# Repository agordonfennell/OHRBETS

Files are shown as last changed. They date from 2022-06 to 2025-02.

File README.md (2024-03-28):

# OHRBETS (Open-source Head-fixed Rodent Behavior Experimental Training System)
<p align="center">
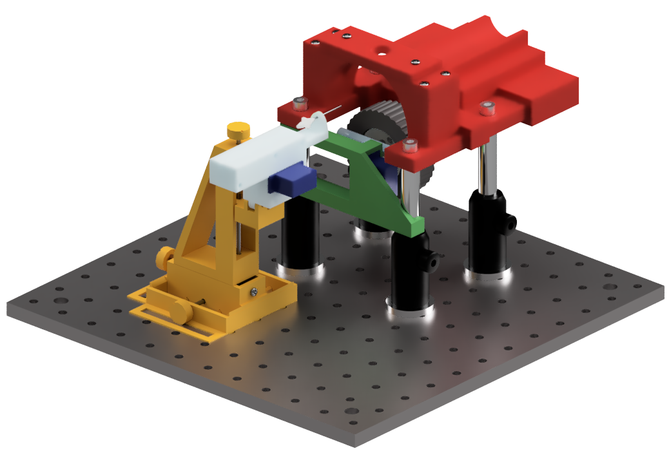
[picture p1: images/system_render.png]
  
</p>

Accompany to [Gordon-Fennell et. al. 2023 eLife](https://elifesciences.org/articles/86183)

## Overview
Here we make available an ecosystem of open-source hardware and software for operant and consumption experiments in head-fixed mice. For operant responding, mice rotate a wheel in one of two directions and operant responding is gated using a mechanical wheel break. For consumption, mice consume liquid solutions from a metal lick spout and access to the spout is gated using retraction and extension of the spout. The system also includes optional multi-spout hardware that allows fixed access to 1 of 5 spouts. The system presented here offers a scalable option for these behavioral approaches and is compatible with head-fixed imaging techniques including 2-photon imaging.  

The hardware consists of 3d printed and other low-cost components including micro servos that can be easily assembled with our detailed step-by-step guide. The system utilizes an Arduino Mega to control hardware including servos, solenoids, and tone generators, and to record behavioral events including licks and wheel rotation. Session parameters and behavioral events are recorded using a PC connected to the Arduino via USB. 

The Arduino software includes programs written in the Arduino language. We have included multiple scripts for different behavioral approaches including operant conditioning and multi-spout brief access. We have also included scrips used to setup for behavior and trouble shoot the system.  

The Analysis software includes programs written in R and relies on user created spreadsheets. We have included a universal decoder that parses the data produced by the Arduino. We have also included scripts for analyzing data produced by the generic operant conditioning and multi-spout brief access task Arduino programs.

We will continue to update this repository and add additional hardware and software. We welcome contributions that add on to our system for different behavioral designs.  
## DOI: 
- 10.5281/zenodo.8320175

## Associated Pre-Print
- [bioRxiv](https://www.biorxiv.org/content/10.1101/2023.01.13.523828v1)

## Up to Date Resources
- [Purchase List](https://docs.google.com/spreadsheets/d/1kFgsOy1gAFHM2E8M-DSgPSi6Y7Lr8sis6cbQqSb2ZY4)
- [3d Printing File Key](https://docs.google.com/spreadsheets/d/1pzRUh2JkpAaJyb1kA9NBVjSYz8nG3GPTu3c0QVQwKCg)

## Tinkercad Models (#OHRBETS)
- [Full Respository](https://www.tinkercad.com/users/elZH8v8MJf0-adam-gordon-fennell)
- [OHRBETS_assembly](https://www.tinkercad.com/things/58vTdDu0pfz)
- [OHRBETS_components_filament](https://www.tinkercad.com/things/1Yv3k1L5hwq)
- [OHRBETS_components_resin](https://www.tinkercad.com/things/6Ztq3dLU4Uj)
- [OHRBETS_components_multispout](https://www.tinkercad.com/things/cckeigB3ydE)
- [OHRBETS_arduino_enclosure](https://www.tinkercad.com/things/ki4dcN9vabO)
- [OHRBETS_mount_syringe](https://www.tinkercad.com/things/ft7A0Lh4chg)
- [OHRBETS_mount_solenoid](https://www.tinkercad.com/things/eRxwZDRHmDL)

## Contributors
Adam Gordon-Fennell (University of Washington), Garret Stuber (University of Washington)

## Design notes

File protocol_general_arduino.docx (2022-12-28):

# General Arduino Protocol

This document contains a general overview of using Arduino and a brief review of the types of scripts that we include with the system.

A detailed overview of the Arduino language and program structure are beyond the scope of this protocol. For a more detailed overview refer to the Arduino website (link (https://www.arduino.cc/reference/en/)).

## General Overview

- Arduinos operates independently of the computer connected to it. Once a script is uploaded to the Arduino, the script will run continuously until the Arduino is loses power or is reset.
- Arduinos can be reset through the following methods
  - Opening a serial connection with the Arduino (e.g. opening the serial monitor in the Arduino IDE or opening a serial connection through python).
  - Connecting and disconnecting the USB
  - Reset button on the Arduino

Note: Make sure you are aware of the current state of the Arduino program. When using behavioral programs, reset the Arduino prior to head-fixing a subject to ensure that the program is in the starting state.

- Each script we have included with this system is composed of 3 major sections
  - Definitions:
    - Each variable is defined. Crucially, the datatype must be set as the variable is defined and will limit the range of values the variable can represent.
    - Dependencies are included
    - Values for many parameters are set
  - void setup ():
    - code that is ran once from top to bottom
    - Behavioral scripts include a line that waits for a serial command from the computer to begin.
  - void loop ():
    - code that is ran repeatedly from top to bottom

## IDE Overview

Serial Monitor

### Main screen

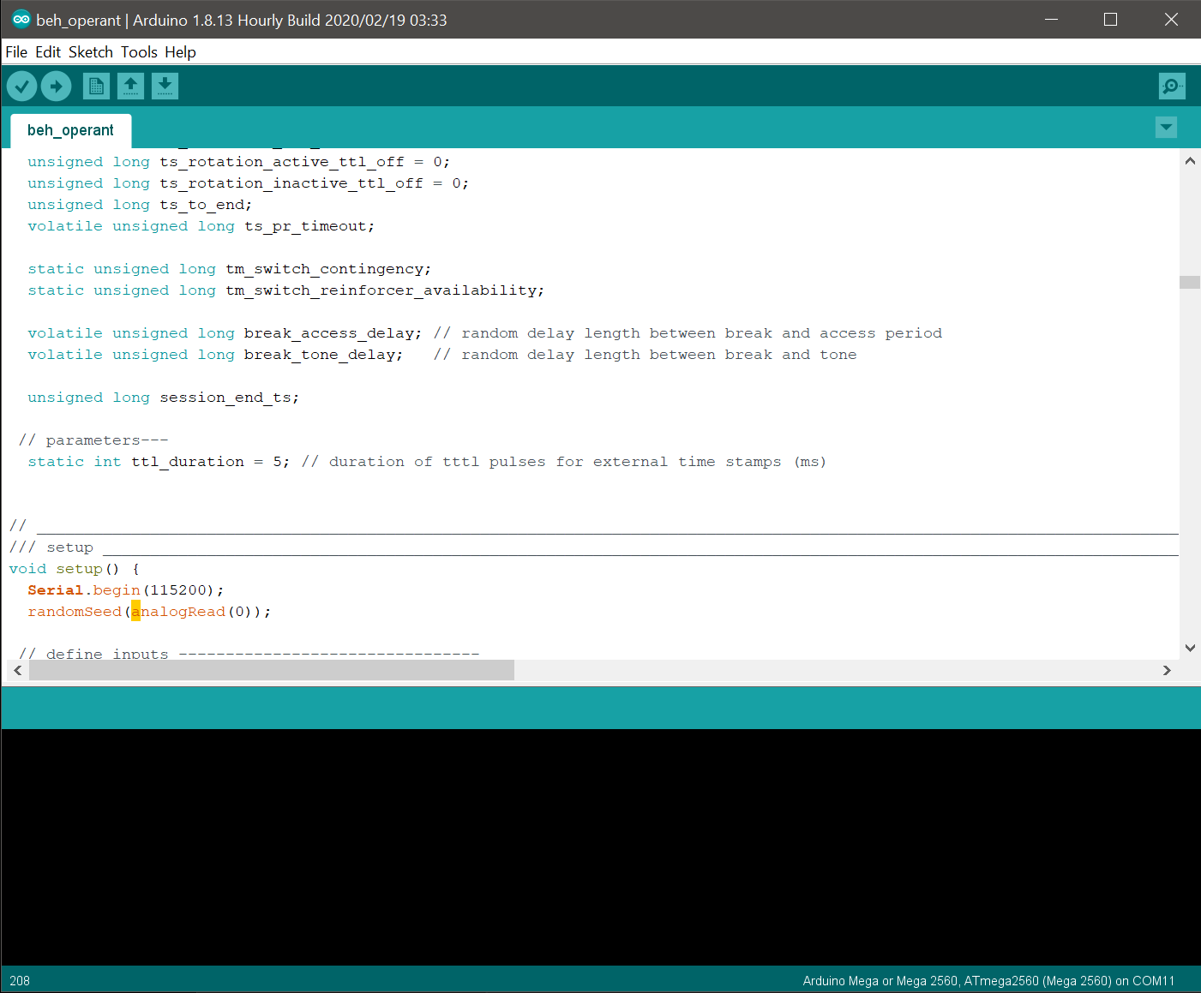
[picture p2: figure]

Upload (Verify script and send to current Arduino)

Verify (check for Arduino syntax)

COM for current Arduino

Arduino Script

Serial Monitor

### Tools menu

Manage libraries to download external libraries

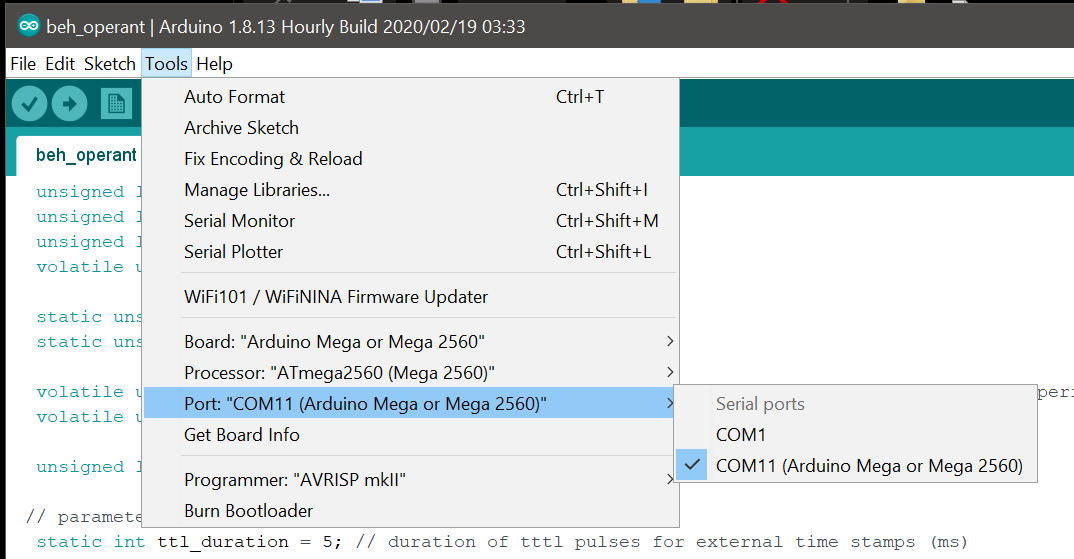
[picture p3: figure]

Set board type of current Arduino

Set current Arduino based on COM port

## Scripts and Serial Monitor Overview

- Arduino scripts (suffix = .ino) must be contained within folders of the same name as the file.
- To open an Arduino script, double click on the .ino file.
- To send script to Arduino, click the “Upload” button
  - You cannot send an script to an Arduino with an active serial connection from another instance of the IDE or external program. Make sure to close these out before attempting to send script to the Arduino.
- To interact and/or monitor the Arduino, click the Serial Monitor button
  - This will connect to the Arduino and reset the script currently on the Arduino (edits to the script will not be reflected on the Arduino until the script is uploaded).
- Serial Monitor

Button to send string to Arduino

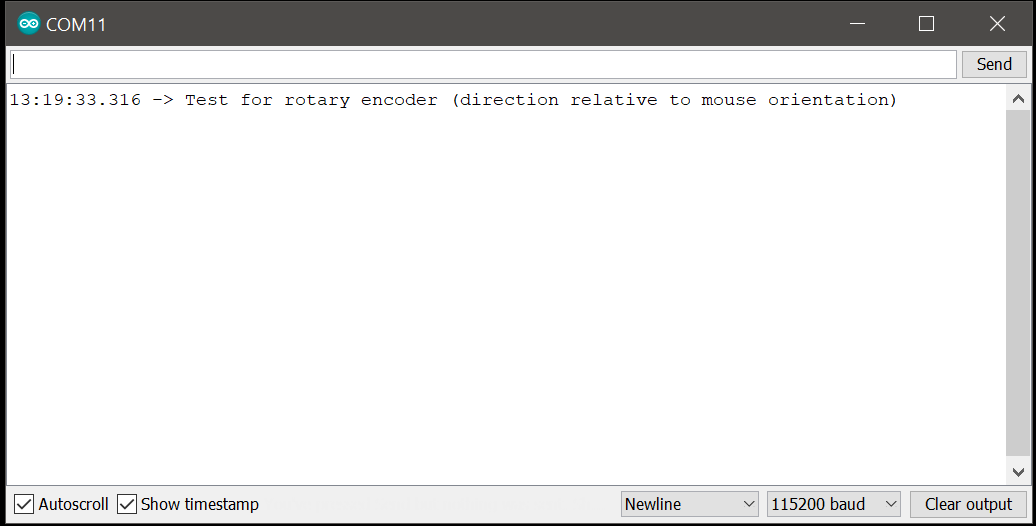
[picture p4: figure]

Baud rate for serial communication

String to send

to Arduino

Display for serial prints from Arduino

  - Multiple “helper” scripts use the Serial Monitor string input to control the state of the Arduino. To do this, simply type out a string in the box to the left of the “Send” button and click Send to communicate it to the Arduino.
- Check to ensure that the baud rate is set correctly.
  - Baud rate is set within the Arduino program with Serial.begin(baudrate)
  - For programs included with this system, the default baud rate is set to 115200. Other scripts may use different buad rates.
  - If the baud rate is not set correctly, the strings produced by the Arduino will not be decoded properly and will be printed with jumbled symbols

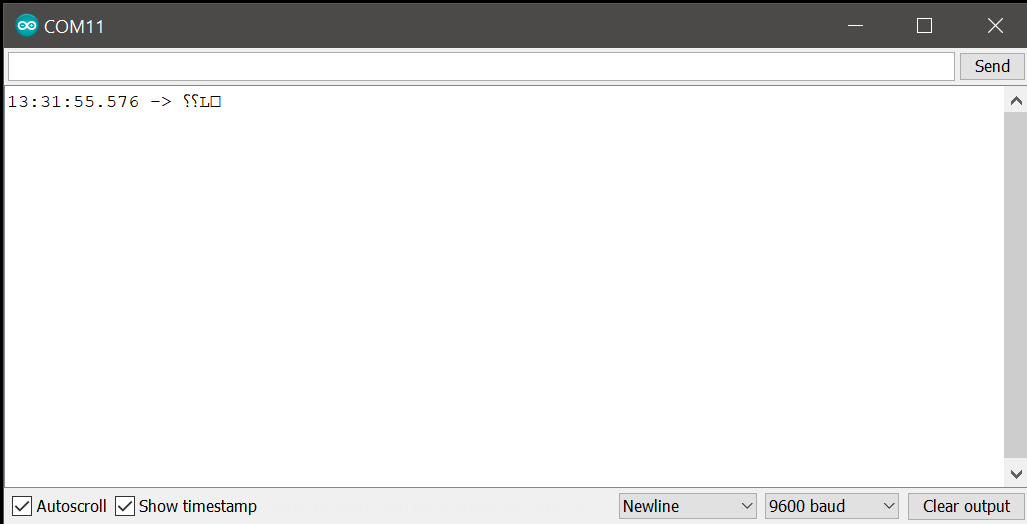
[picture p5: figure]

- Behavioral scripts will require that a string is sent to the Arduino before the program begins
  - For testing a program, open the Serial Monitor and click the “Send” button to send an empty string and start the behavioral program.
  - During real behavioral sessions, we will use a python script to open the serial connection, start the Arduino, and record the serial (see Python section below).

## External libraries

- You will need to install the MPR121 library in order to compile and upload scripts that contain lick detection.
  - Installed through Tools > Manage Libraries > search MPR121

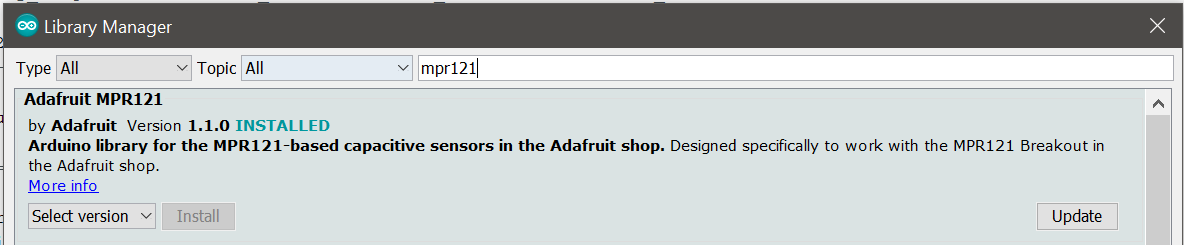
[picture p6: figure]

  - Make sure to install with all dependencies

## write_serial.py Overview

- The write_serial.py script is used to restart the Arduino, send a start command, and then record the Serial prints while the Arduino is running.
- Can be run using any IDE or directly from the command line. We used Sublime Text 3 for the example shown here.
- There are 3 parameters that you will need to set:

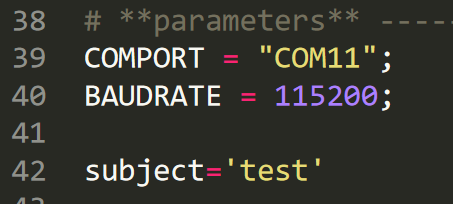
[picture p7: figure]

  - COMPORT: string identifier for the comport of the Arduino (check the Arduino Tools > Port for Com ID)
  - BAUDRATE: integer baud rate (must match comport set in Arduino script)
  - Subject: string for subject ID (must be unique for each session)
- When executed the program will do the following
  - Generate file name based on current date and subject id:
    - General format: yyyy_mm_dd_subject
    - If there is a conflict, a string suffix will be added for the time with the following format: _hhmmss
  - Open serial communication with Arduino based on COMPORT and BAUDRATE
  - Generate and then append a csv file with each line printed by the Arduino each
    - Note: the program only works with numeric and space prints from the Arduino and will not work with strings of characters
  - Closes serial communication and stops executing when a “0” is printed in the first position of the print from the Arduino.
    - Note: If you edit the Arduino scripts, do not include a print with 0 in the first position

## Raw data structure

All behavioral programs are written to have a uniform data structure consisting of two columns of numerical data that fall into 3 categories

1. Parameters: stable parameters for the session (1 row). These values print once at the start of the session.
  a. First column: parameter ID
  b. Second column: parameter value
2. Dynamic parameters: parameters can change values at different points throughout a session (2 rows / change in parameter)
  a. First column first and second rows: parameter ID
  b. Second column first row: time stamp for the onset of the current parameter (ms)
  c. Second column second row: current value of the parameter
3. Events: events occurring during the behavioral session
  a. First column event ID
  b. Second column timestamp (ms)
- All of the IDs for events, parameters, and dynamic parameters are listed in key_events.csv. This table is used to decode data within each raw Arduino csv file.
  - If you add additional events, follow the format outlined here in the Arduino print, and add a corresponding row to the key_events.csv file.

## Trouble shooting quick guide:

- Cannot upload script to Arduino

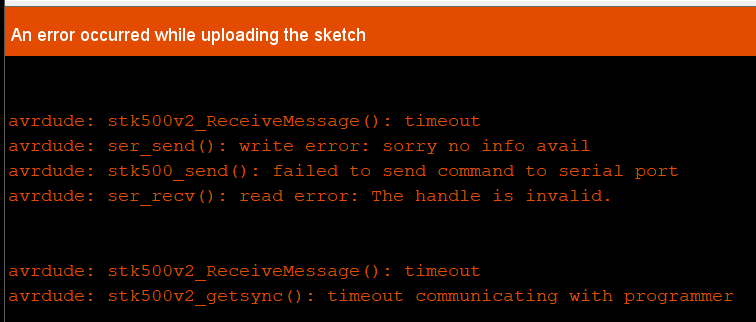
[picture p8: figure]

  - Check to ensure that all other serial communication with the Arduino is closed. If the problem persists, disconnect / reconnect Arduino USB
- Strange symbols in serial print via Serial Monitor
  - check baud rate in script and serial connection
- Cannot connect to Arduino with write_serial.py

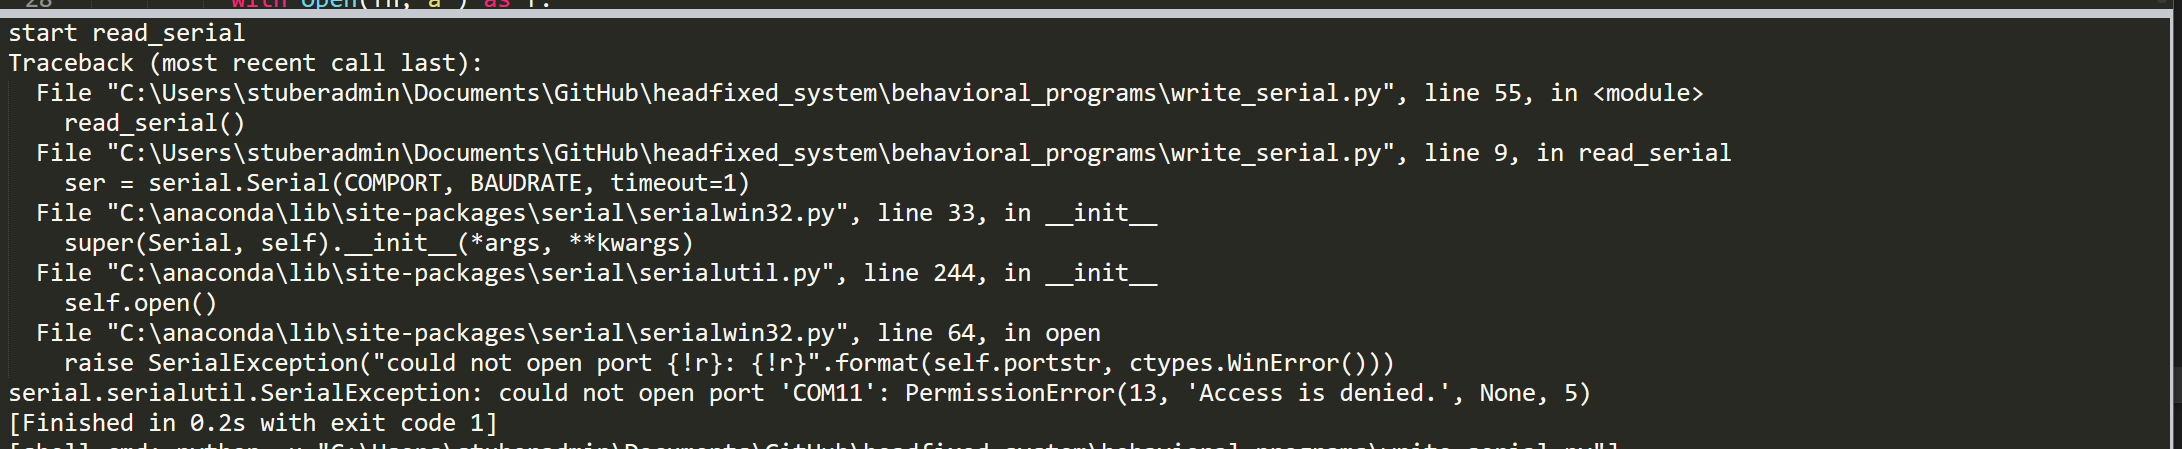
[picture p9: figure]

  - Check to ensure that all other serial communication with the Arduino is closed. If the problem persists, disconnect / reconnect Arduino USB
  - Check to ensure that COMPORT is set to the correct Arduino
- UnicodeDecodedError with write_serial.py

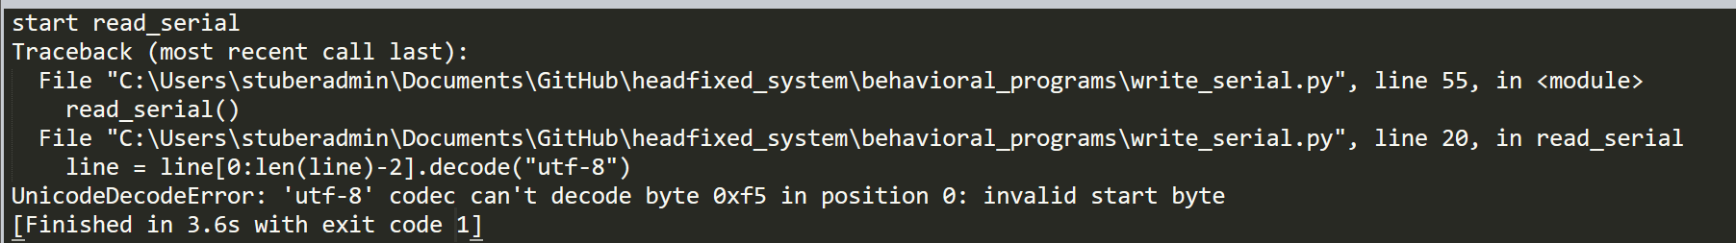
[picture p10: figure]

  - Check to ensure that baud rate in write_serial.py matches baud rate set in Arduino script
  - Check to ensure that COMPORT is set to the correct Arduino

Write_serial.py Arduino script

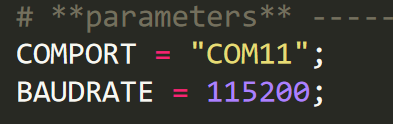
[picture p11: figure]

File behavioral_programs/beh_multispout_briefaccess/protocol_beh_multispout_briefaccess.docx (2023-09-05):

Protocol for beh_multispout_briefaccess.ino

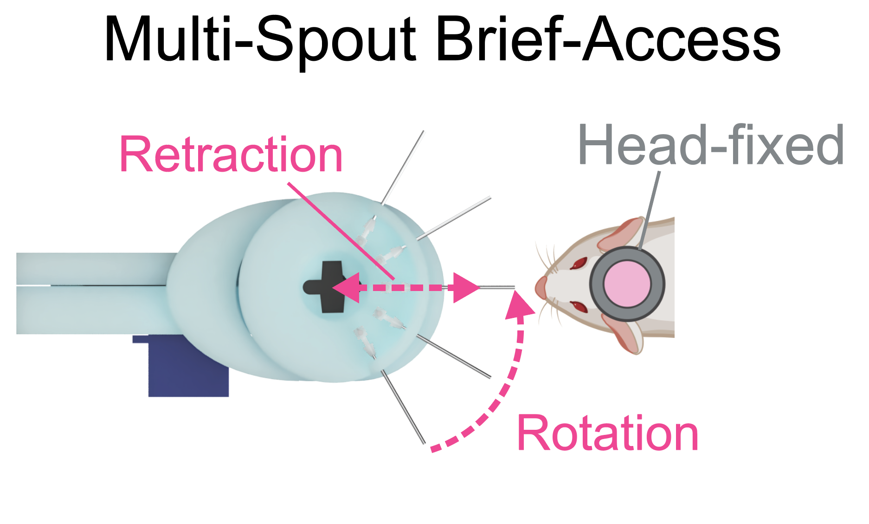
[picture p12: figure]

Program purpose: allows subject fixed windows of access time to one of multiple spouts.

Access windows can include free-access consumption or fixed volume delivery.

Preparation Instructions:

1) Around once per week, calibrate the solenoid open duration for each solenoid by following protocol_helper_calibratesolenoid. Save the solenoid open duration(s) somewhere convenient in a vector format with 1 value per solenoid (e.g. 3 elements for 3 spouts: each vector would look like {value, value, value}).
2) Fill the solution line(s) by following protocol_helper_opensol.
3) Optional: connect BNC or TTL outputs from the arduino console to the external hardware.

Initial Calibration of Rotation and Extension

After assembling the hardware, it is useful to perform an initial calibration to determine estimates for the rotation and extension of each spout. These values will serve as a starting point but may be changed slightly at the start of each day.

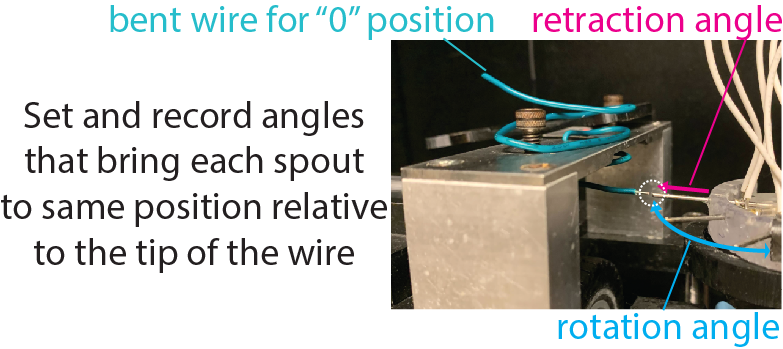
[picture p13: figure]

1. Use a length of wire and wrap it over a head stage such that the end of the wire sits roughly where the nose of a mouse would be located.
2. Upload manual_servo.ino and open the Serial Monitor.
3. First, fully extend the retractable spout.
  1. Enter the pin for the servo used for retraction and send over serial (default = 9).
  2. Enter 180 for a fully extended starting position.
4. Next, move the servo to determine the rotation angle for each spout.
  1. Enter the pin for the servo used for the radial multi-spout head and send over serial (default = 11).
  2. Rotate the head to the first spout (right most spout from the mouse’s perspective) so it is at a right angle relative to the head-stage. Start with sending a value of 0 over the serial, then progressively increase until the spout is at a right angle. Record this value.
  3. Use the micro-positioner to move the spout so it is in line with the piece of wire and almost touching.
d. For the remaining spouts, send new serial values to change the rotation of the head to align each spout with the tip of the wire and record the angle for each spout (you should have one angle for each spout). With default hardware, the spouts should be roughly 30 degrees apart.
5. To calibrate the extension for each spout
  1. Open the beh_multispout_briefaccess.ino program.
  2. Enter the servo_radial_degs values obtained from step 4 (format: {#,#,#};, with one # for each spout).
  3. Enter default values for servo_retract_extended_degs ({180,180,180}; with one value for each spout).

Arduino Setup Instructions:

1) Open the program
2) Set the parameters and input / output pins
- Carefully read the comments next to each variable
3) Upload script to arduino by clicking the “Upload” arrow button on the top left corner
- The arduino will now have the script running on it and it will wait until a start command is sent over serial.

Arduino Test Instructions:

Test the program at the start of each day to ensure all hardware is working and events are being recorded correctly.

1) To test the program, open serial monitor by clicking the “Serial Monitor” button on the top right corner

Note: If you do not see this text printed in the serial monitor, see troubleshooting arduino software document.

2) Start the arduino program by clicking the button to send an empty string over serial.

### Note on lick detection with high-molar NaCl

Special care needs to be taken to ensure that the capacitive touch sensor is accurately detecting licks when using high-molar NaCl solutions. Some systems have produced poor detection on specific spouts during mouse licking. After confirming that all hardware works with finger touches, watch subject licking carefully while monitoring lick detection. If there is a problem with lick detection on a particular spout, do not use this spout for high molar NaCl or build a new multi-spout head. Future improvements to the design will be posted in the accompanying GitHub.

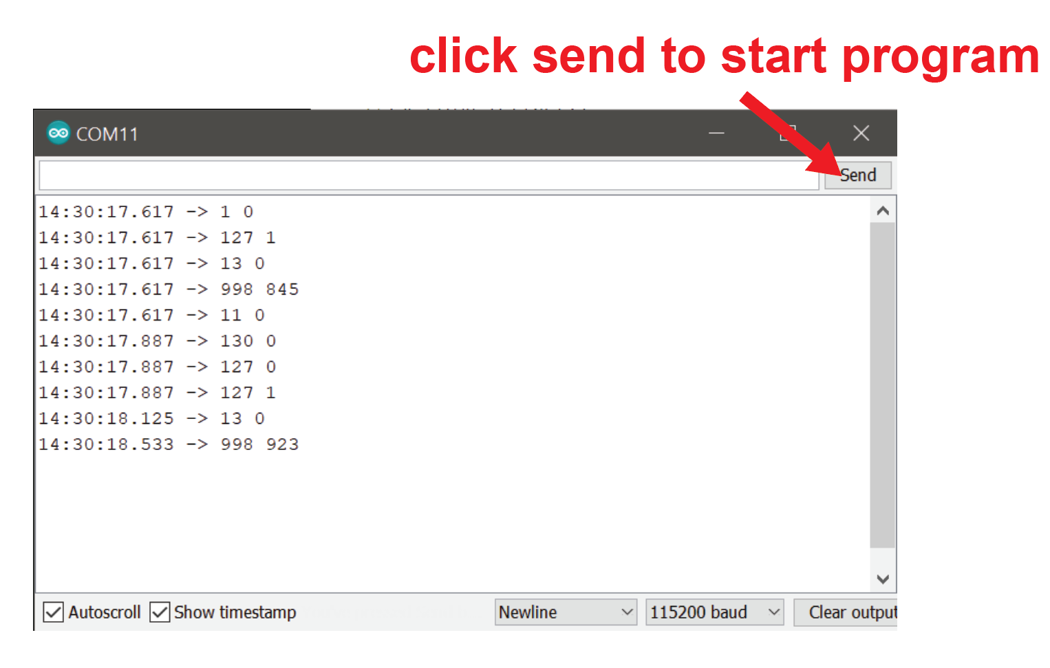
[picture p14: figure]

3) Watching the Serial Monitor while interacting with the hardware, check to ensure that…
  a) Rotating the wheel in the intended active direction produces code 81.
  b) Rotating the wheel in the intended inactive direction produces code 71.
  c) Touching the spout produces code 30 + current spout (e.g. 31 for spout 1, 32 for spout 2, etc.).
  d) Rotation of the wheel in the active direction that reaches the fixed ratio triggers the intended sequence of events (break, tone, spout extension, liquid delivery or external TTL signal).
  e) If performing progressive ratio, check to ensure that the cost of the reinforcer increases as intended.
  f) Rotation in the inactive direction that reaches the fixed ratio triggers the intended sequence.
4) For multi-spout systems, if the intended spout is not detecting touch, check other spouts to see if they are detecting touch. If you find that a spout other than the one rotated towards the mouse is detecting touch, then check the servo_retract_radial_degs vector to ensure the values are correct for your head, and check to ensure the servo is working properly.
  a) If liquid is emerging from the wrong spout, then check the pinSol vector to ensure that the correct pins are included for your system.
5) Reset the arduino by closing and reopening the Serial Monitor, and then close Serial Monitor prior to the session.

Arduino Run Instructions:

1) Open the write_serial.py program (shown here using Sublime Text 3)

- Set the COMPORT and BAUDRATE to match the arduino script

Arduino comport is shown in the tools drop down menu

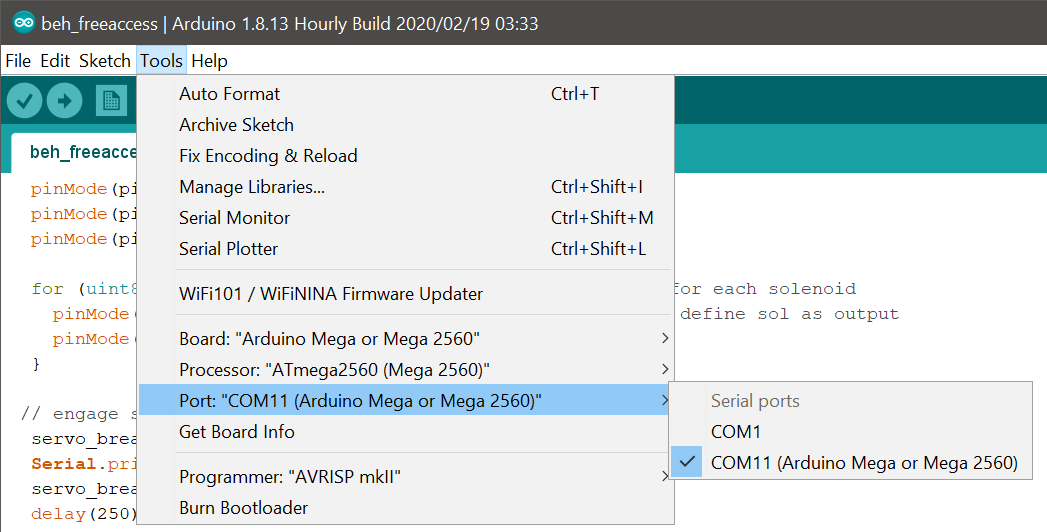
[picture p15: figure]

Arduino baudrate is set with “Serial.begin” call

- Set the subject name for the session in the python program

Note: See general arduino software document for more details about the functionality of the write_serial.py program.

2) After the program and hardware have been tested, head-fix the animal.
3) Set the spout position as shown in this diagram:

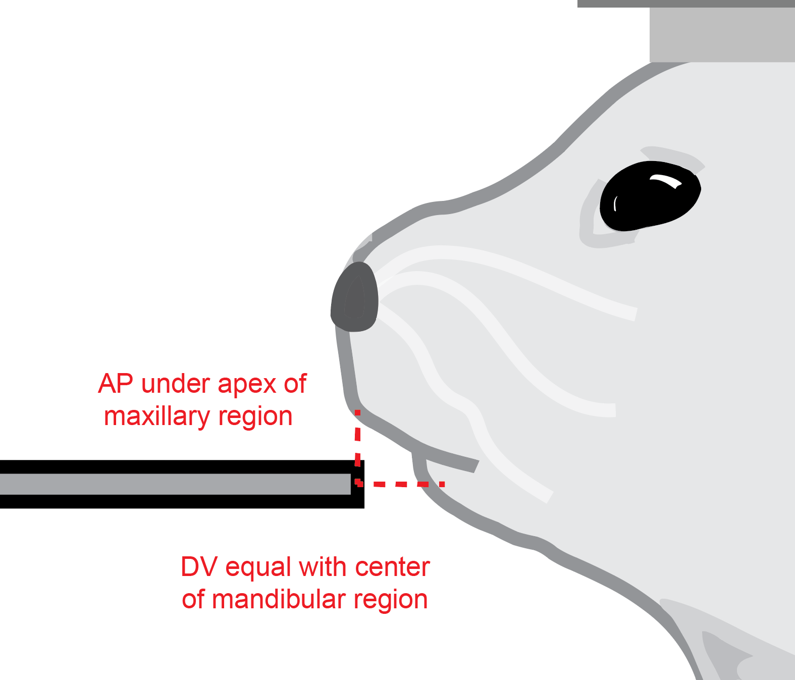
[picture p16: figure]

Note: See link (https://www.facebase.org/mouseanatomy/) for examples of mouse face anatomy

4) Run the python program (Cntrl + B for Sublime Text 3).
- Values should begin to print with the start of the session, and will continue to print during recorded events.

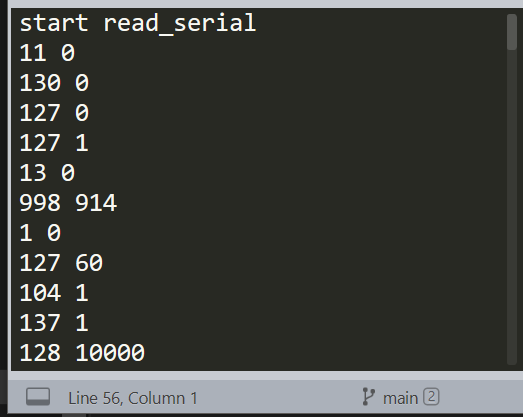
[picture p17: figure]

Note: If you see an error, refer to the general arduino software document for troubleshooting tips.

5) At the end of the session, the spout will retract (if using a retractable spout), the brake will engage, and the python script will print “stop read_serial”).
6) Remove subject from head-fixation.
7) Restart arduino prior to subsequent subjects by opening / closing the arduino Serial Monitor. Otherwise, the spout will extend for the next subject and could result in poking the subject.

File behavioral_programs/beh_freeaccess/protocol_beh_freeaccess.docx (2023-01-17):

Protocol for beh_freeaccess.ino

Program purpose: free-access consumption for a set session duration.

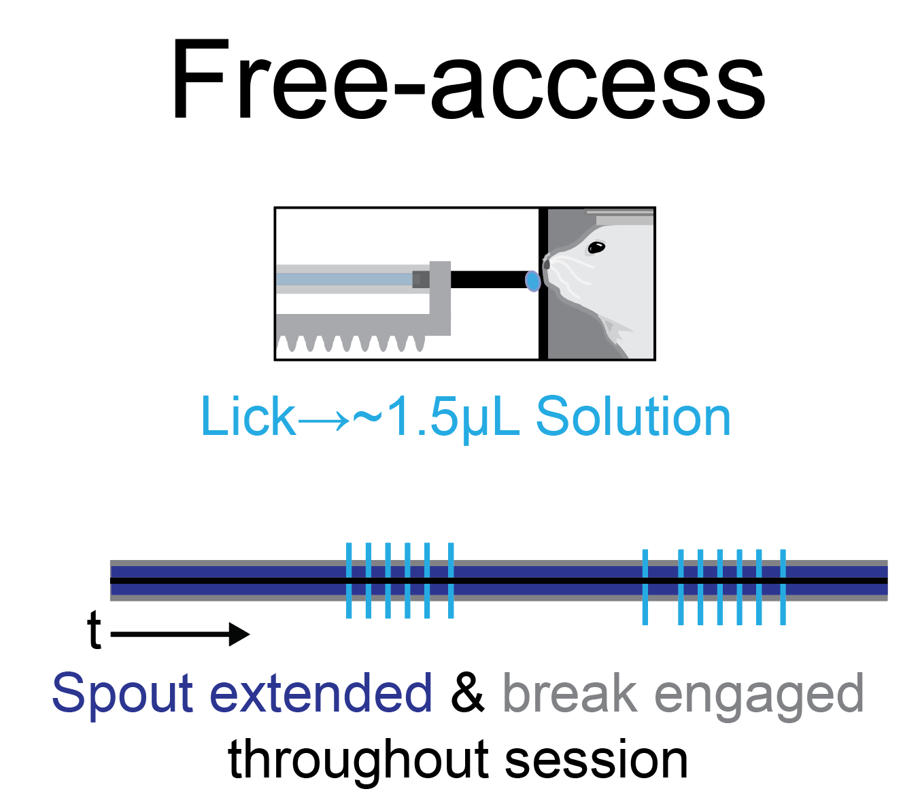
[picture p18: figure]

Preparation Instructions:

1) Around once per week, calibrate the solenoid open duration by following protocol_helper_calibratesolenoid. Save the solenoid open duration(s) somewhere convenient in a vector format with 1 value per solenoid (e.g. 3 vectors for 3 spouts: each vector would look like {value, value, value}).
2) Fill the solution line(s) by following protocol_helper_opensol.
3) Optional: connect BNC or TTL outputs from the arduino console to the external hardware.

Arduino Setup Instructions:

1) Open the program
2) Set the parameters and pins

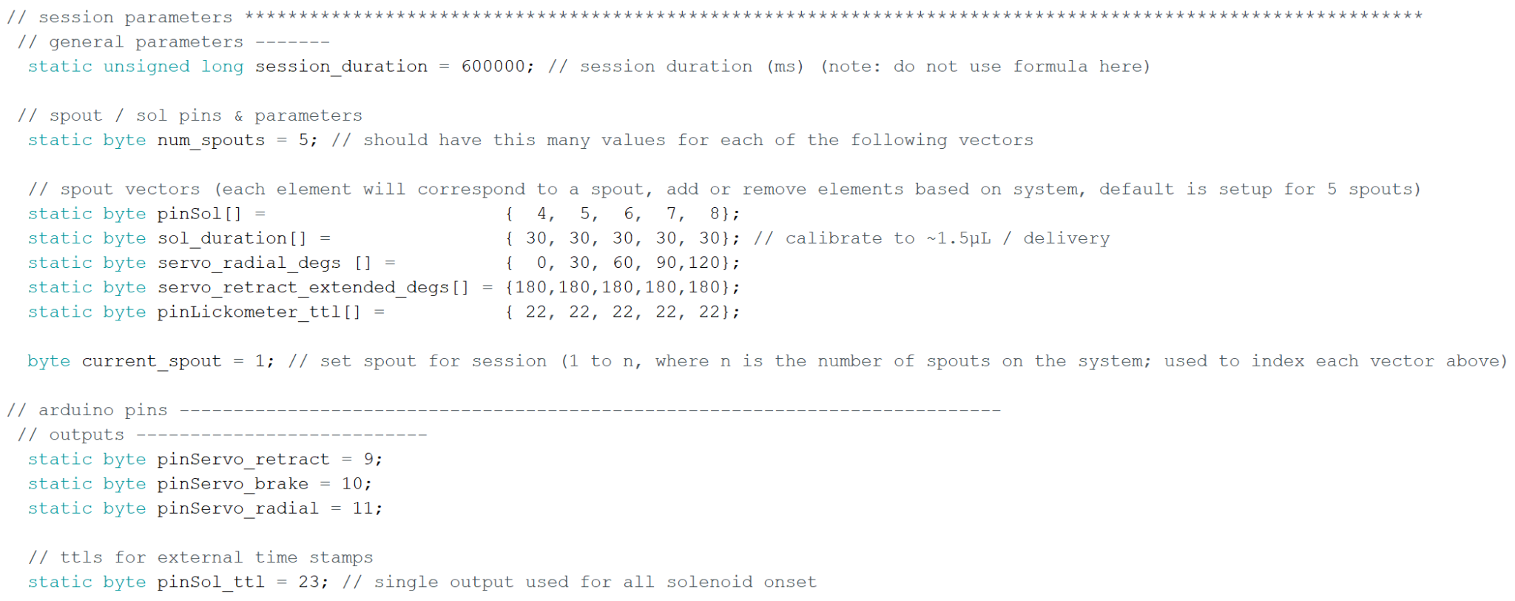
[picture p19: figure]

- For spout / sol pins & parameters, you will need 1 value for each of the spout / sol that your system has. This way you can set current_spout to perform free-access licking on any spout (e.g. current_spout 1 uses the first value for each vector, current_spout 2 uses the second value, etc.).
  - Note: If your system only has 1 spout, then change the vectors to be a length of 1 (e.g. pinSol[] = {4}; sol_duration[] ={30}; etc. ).
- It is fine if you do not have a radial servo, as long as nothing is plugged into the corresponding pin
- pinLickometer_ttl is used as an external timestamp for the onset of licks on each spout
- pinSol_ttl is used as an external timestamp for onset of any solenoid opening
3) Upload script to arduino by clicking the “Upload” arrow button on the top left corner.
- The arduino will now have the script running on it and it will wait until a start command is sent over serial.

Arduino Test Instructions:

Test the program at the start of each day to ensure all hardware is working and events are being recorded correctly.

1) To test the program, open the serial monitor by clicking the “Serial Monitor” button on the top right corner.

Note: If you do not see this text printed in the serial monitor, see troubleshooting arduino software document.

2) Start the arduino program by clicking the button to send an empty string over serial.

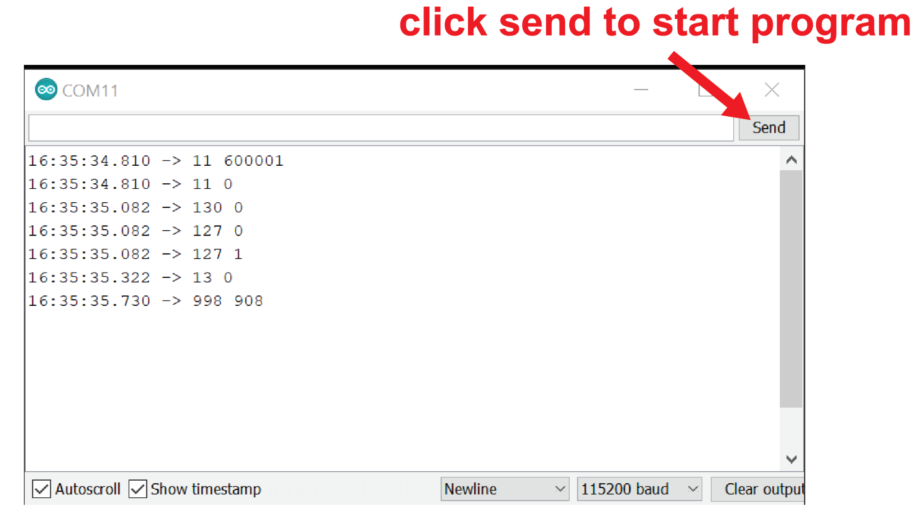
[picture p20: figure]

3) Manually touch the spout gently with the tip of an ungloved finger several times to ensure that licks are being detected, solenoids are opening, and liquid is being delivered from the lick spout. Each touch on the current_spout should lead to events printed in the Serial Monitor, opening of the corresponding solenoid (confirmed with concurrent sound, or vibrations when solenoid is touched during opening), and a droplet of liquid emerging from the spout.
  a) The serial code should be 30 + current_spout (e.g. if current_spout = 2, then the code should be 32).
  b) For multi-spout systems, if the intended spout is not detecting touch, check other spouts to see if they are detecting touch. If you find that a spout other than the one rotated towards the mouse is detecting touch, then check the servo_retract_radial_degs vector to ensure the values are correct for your head, and check to ensure the servo is working properly
  c) If liquid is emerging from the wrong spout, then check the pinSol vector to ensure that the correct pins are included for your system.
4) Reset the arduino by closing and reopening the Serial Monitor. Close Serial Monitor prior to the session.

Arduino Run Instructions:

1) Open the write_serial.py program (shown here using Sublime Text 3)

- Set the COMPORT and BAUDRATE to match the arduino script

Arduino comport is shown in the tools drop down menu


Arduino baudrate is set with “Serial.begin” call

- Set the subject name for the session within the python program

Note: see general arduino software document for more details about the functionality of the write_serial.py program

2) After the program and hardware have been tested, head-fix the animal.
3) Set the spout position as shown in this diagram:


Note: See link (https://www.facebase.org/mouseanatomy/) for examples of mouse face anatomy

4) Run the python program (Cntrl + B for Sublime Text 3).
- Values should begin to print with the start of the session, and will continue to print during recorded events


Note: If you see an error, refer to the general arduino software document for troubleshooting tips

5) At the end of the session, the spout will retract (if using a retractable spout) and the python script will print “stop read_serial”
6) Remove subject from head fixation
7) Restart arduino prior to subsequent subjects by opening / closing the arduino Serial Monitor. Otherwise, the spout will extend for the next subject and could result in poking the subject

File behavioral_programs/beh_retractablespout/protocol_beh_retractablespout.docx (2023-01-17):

Protocol for beh_retractablespout.ino

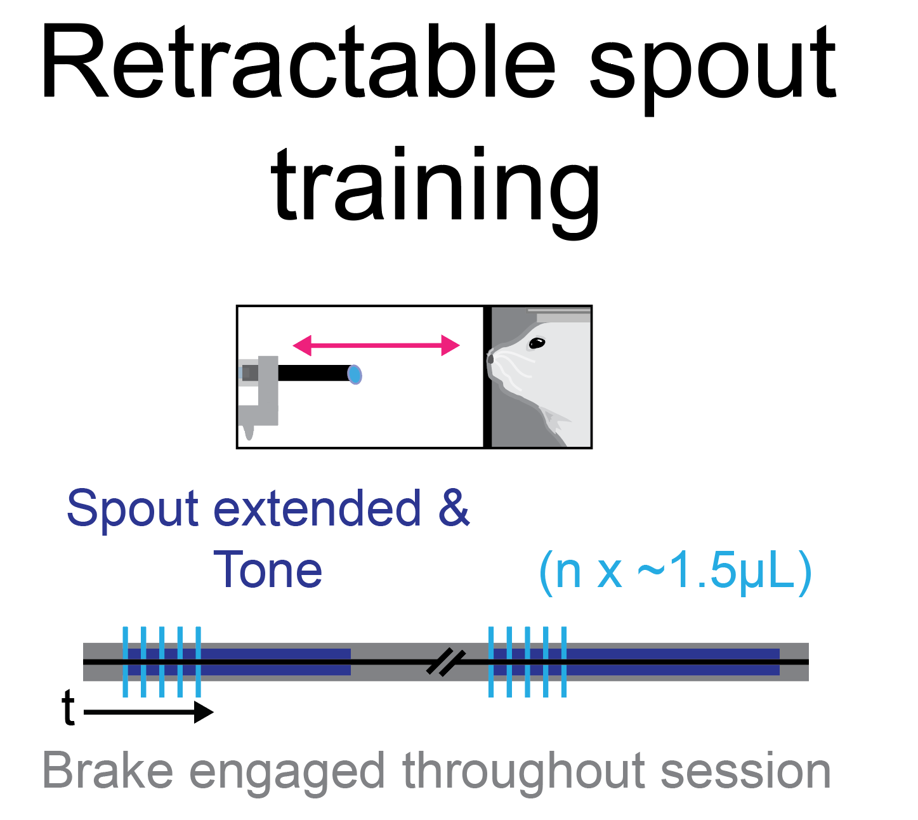
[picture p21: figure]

Program purpose: delivery of a fixed volume of solution with options for retractable spout training and Pavlovian Conditioning.

Preparation Instructions:

1) Around once per week, calibrate the solenoid open duration by following protocol_helper_calibratesolenoid. Save the solenoid open duration(s) somewhere convenient in a vector format with 1 value per solenoid (e.g. 3 values for 3 spouts: each vector would look like {value, value, value}).
2) Fill the solution line(s) by following protocol_helper_opensol.
3) Optional: connect BNC or TTL outputs from arduino console to external hardware

Arduino Setup Instructions:

1) Open the program
2) Set the parameters and pins (see Arduino script for all parameters / comments)

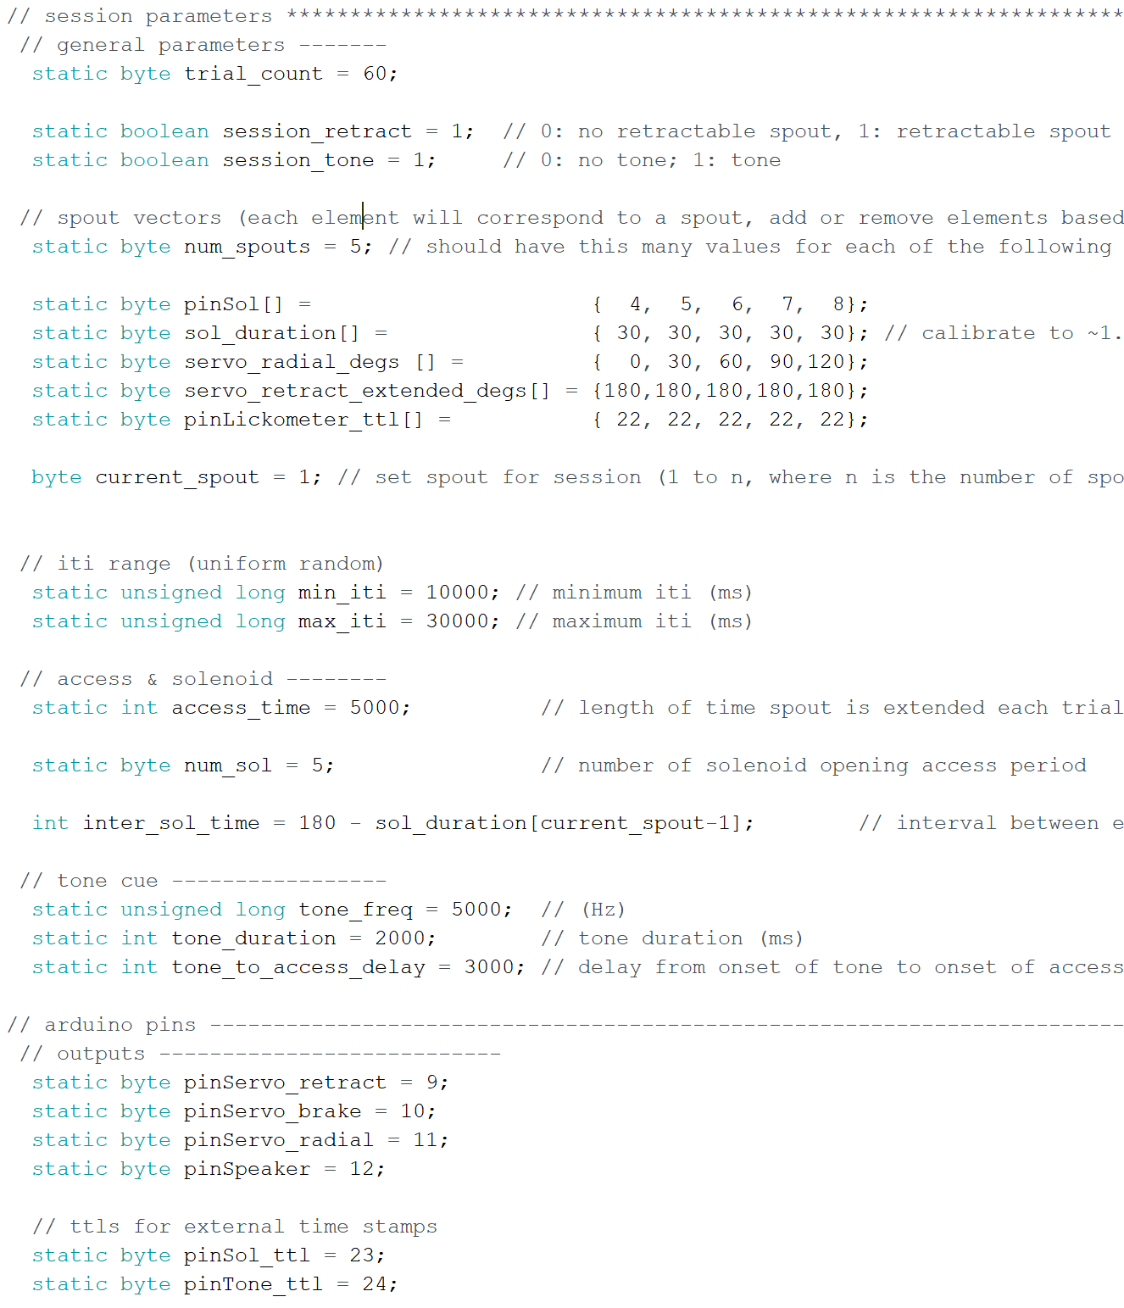
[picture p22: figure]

- Use the tone_duration and tone_to_access_delay to set up the timing for tones and access period / liquid delivery.
- For spout / sol pins & parameters, you will need 1 value for each of the spout / sol that your system has. This way you can set current_spout to perform free-access licking on any spout (e.g. current_spout 1 uses the first value for each vector, current_spout 2 uses the second value, etc.).
  - Note: If your system only has 1 spout, then change the vectors to be a length of 1 (e.g. pinSol[] = {4}; sol_duration[] ={30}; etc.).
- It is fine if you do not have a radial servo, so long as nothing is plugged into the corresponding pin.
- pinLickometer_ttl is used as an external timestamp for onset of licks on each spout.
- pinSol_ttl is used as an external timestamp for onset of any solenoid opening.
- pinTone_ttl is used as an external timestamp for the tone (high for the duration of the tone).
3) Upload script to arduino by clicking the “Upload” arrow button on the top left corner
- The arduino will now have the script running on it and it will wait until a start command is sent over serial.

Arduino Test Instructions:

Test the program at the start of each day to ensure all hardware is working and events are being recorded correctly.

1) To test the program, open serial monitor by clicking the “Serial Monitor” button on the top right corner

You should then be presented with this screen:

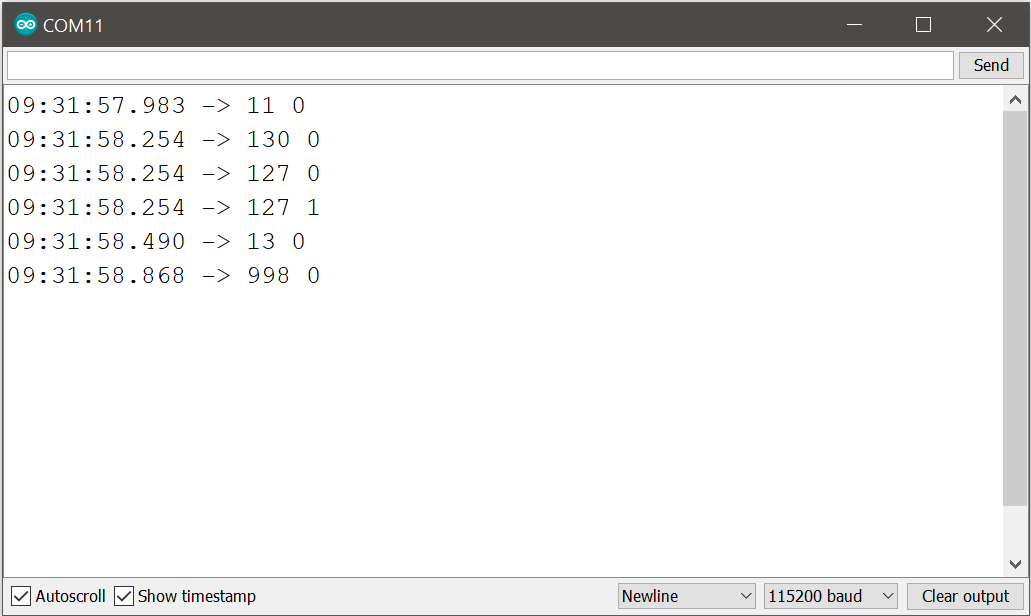
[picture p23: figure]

Note: If you do not see this text printed in the serial monitor, see troubleshooting arduino software document.

2) Start the arduino program by click the button to send an empty string over serial


3) Wait for the trial to begin (tone indicated with code 51, spout extension with code 13, solenoid opening with 18) and check to ensure that liquid is coming out of the tip of the spout. Next, manually touch the spout gently with the tip of an ungloved finger several times to ensure that licks are being detected (indicated with code 30 + current_spout).
  a) For multi-spout systems, if the intended spout is not detecting touch, check other spouts to see if they are detecting touch. If you find that a spout other than the one rotated towards the mouse is detecting touch, then check the servo_retract_radial_degs vector to ensure the values are correct for your Multi-Spout Head, and check to ensure the servo is working properly.
  b) If liquid is emerging from the wrong spout, then check the pinSol vector to ensure that the correct pins are included for your system.
4) Reset the arduino by closing and reopening the Serial Monitor, and then close Serial Monitor prior to the session.

Arduino Run Instructions:

1) Open the write_serial.py program (shown here using Sublime Text 3)

- Set the COMPORT and BAUDRATE to match the arduino script

Arduino comport is shown in the tools drop down menu


Arduino baudrate is set with “Serial.begin” call

- Set the subject name for the session within the write_serial.py

Note: See general arduino software document for more details about the functionality of the write_serial.py program

2) After the program and hardware have been tested, head fix the animal.
3) Set the spout position as shown in this diagram:


Note: See link (https://www.facebase.org/mouseanatomy/) for examples of mouse face anatomy

4) Run the python program (Cntrl + B for Sublime Text 3).
- Values should begin to print with the start of the session, and will continue to print during recorded events.


Note: If you see an error, refer to the general arduino software document for troubleshooting tips.

5) At the end of the session, the spout will retract (if using a retractable spout) and the python script will print “stop read_serial”).
6) Remove subject from head-fixation.
7) Restart arduino prior to subsequent subjects by opening / closing the arduino Serial Monitor. Otherwise, the spout will extend for the next subject and could result in poking the subject.

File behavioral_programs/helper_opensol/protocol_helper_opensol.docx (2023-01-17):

Protocol for helper_opensol.io

Program purpose: helper_opensol.io allows users to rotate the Multi-Spout Head and open individual solenoids for set up or cleanup using one of two modes.

- mode 0:
  - touch spout to open corresponding solenoid, touch again to close
  - set multi-spout angle by sending a degree between 1 and 180 over serial
- mode 2:
  - set multi-spout angle using servo_radial_deg
  - open and close solenoids by sending a serial string with an ID between 1 and n, where n is the number of spouts set in pinSol and stateSol

Note: default program is set up for 5 solenoids / spouts, but can be used for 1 solenoid / spout. See “increasing number of solenoids” section below for instructions for expanding the number of solenoids / spouts.

Use Instructions:

1) Open the program (make sure the program is located in a folder of the same name)
2) Set the parameters and pins

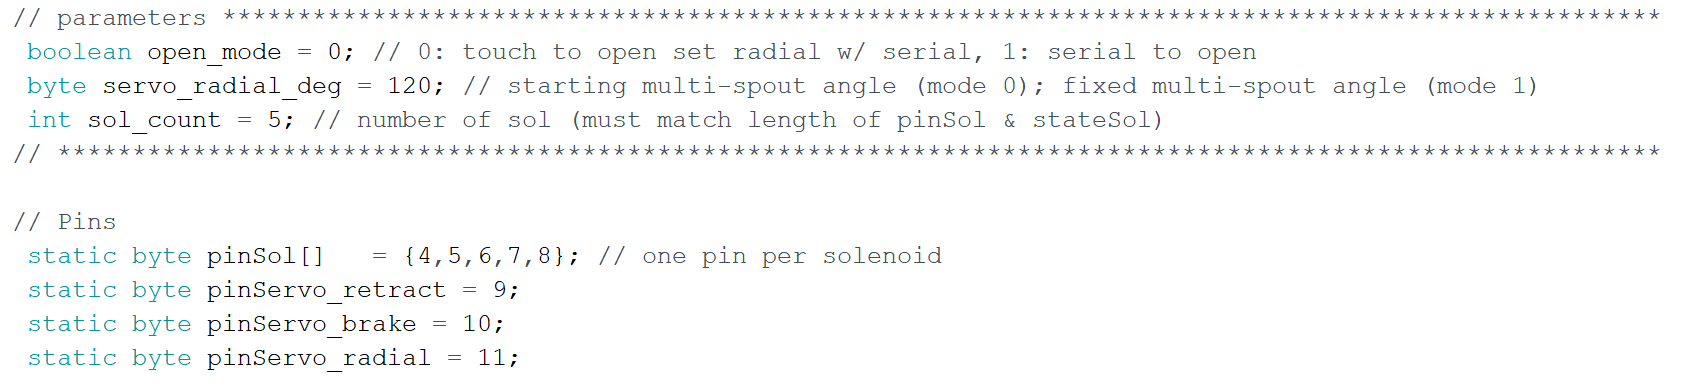
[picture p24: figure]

- Check to ensure that all of the pins correspond to the hardware. For pinSol, it is fine to have more pins listed in pinSol than there are sol, so long as those pins are not connected to anything.
- Set open_mode
  - 0: touch to open (touching spouts 1-n will open corresponding sol 1-n); serial input sets angle of multi-spout head
  - 1: serial to open (serial input of digits 1-n will open corresponding sol 1-n); angle of multi-spout head is set using servo_radial_deg
- Set servo_radio_deg
  - Mode 0: starting position
  - Mode 1: set position (reupload script with new value to rotate head)
3) Upload script to arduino by clicking the “Upload” button on the top left corner.
4) Open serial monitor by clicking the “Serial Monitor” button on the top right corner

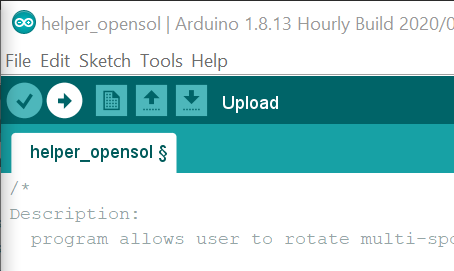
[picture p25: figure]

You should then be presented with this screen


Note: If you do not see “Serial Begin” printed in the Serial Monitor, see general troubleshooting document.

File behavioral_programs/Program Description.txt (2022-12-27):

Behavioral Programs:
 ~these programs are used to conduct behavioral experiments. 
  we have included all of the behavioral experiments presented in 
  Gordon-Fennell et al. 2023, and additional behavioral programs for 
  insperation

 - Operant conditioning
   - options
     * fixed-ratio
     * fixed-ratio, incremental
     * progressive-ratio

 - Real-time place testing

 - Multi-spout, fixed-choice, brief-access

 - Multi-spout, free-choice

Helper Programs:
 ~these programs are used to assist with setting up for behavioral
  experiments

 - helper_opensol
   ~this program is used to manually open solenoids for each spout
    using a touch on the spout or a serial input   

- helper_callibratespout

Scripts:

- generate_trials.py
   - generates string of trial ids for multi-spout, fixed-choice, brief-access

- read_serial.py
   - issues start command to arduino and records serial to a .csv file

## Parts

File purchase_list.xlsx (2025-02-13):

item | retailer | order_quantity | needed_quantity | price | order_number | url | note
aluminum breadboard | ThorLabs | 1 | 1 | 143.92 | 1 | https://www.thorlabs.com/thorproduct.cfm?partnumber=MB1530/M | minimum size, can purchase longer or wider ones for more components
Metal Cabinet | Amazon | 1 | 1 | 123.8 | 1 | https://www.tooldiscounter.com/product/homak-2-door-wall-cabinet-w-2-shelves-homgs00727021 | should be metal
Solderless Breadboard | Amazon | 4 | 1 | 5.99 | 1 | https://www.amazon.com/Pcs-MCIGICM-Points-Solderless-Breadboard/dp/B07PCJP9DY
Capacitive Touch Sensor | Adafruit | 1 | 1 | 7.95 | 1 | https://www.adafruit.com/product/1982
Micro Servo | Adafruit | 1 | 3 | 5.95 | 3 | https://www.adafruit.com/product/169 | 1 for brake, 1 for retractable spout, 1 for radial spout
Piezo Speaker | Adafruit | 1 | 1 | 0.95 | 1 | https://www.adafruit.com/product/1739
Command Strips (64 pack) | Amazon | 64 | 2 | 8.41 | 1 | https://www.amazon.com/Command-Damage-Free-Poster-posters-Packaging/dp/B0751VFF2X?s=hi | used to mount the syringe rack
USB 2.0 A to B | Amazon | 3 | 2 | 10.99 | 2 | https://www.amazon.com/Cable-Matters-3-Pack-USB-Printer/dp/B00UNZ9N6O | purchase 2 for opto
Arduino Mega 2560 Rev3 | Arduino | 1 | 1 | 40.3 | 1 | https://store.arduino.cc/usa/mega-2560-r3
Arduinon Uno Rev3 | Arduino | 1 | 1 | 23 | 1 | https://store.arduino.cc/usa/arduino-uno-rev3 | Optional, used for pulse train generation
Optical Post (75mm) | ThorLabs | 1 | 4 | 5.58 | 4 | https://www.thorlabs.com/thorproduct.cfm?partnumber=TR75/M | can get away with 2 if motion is not a concern
M6 screws (16mm) | ThorLabs | 25 | 10 | 8.87 | 1 | https://www.thorlabs.com/thorproduct.cfm?partnumber=SH6MS16
Washer, M6 Compatible | ThorLabs | 100 | 10 | 4.96 | 1 | https://www.thorlabs.com/thorproduct.cfm?partnumber=W25S050
Breadboard Jumper Wires | Amazon | 120 | 20+ | 5.99 | 1 | https://www.amazon.com/EDGELEC-Breadboard-Optional-Assorted-Multicolored/dp/B07GD2BWPY
Jumper Wires | Amazon | 560 | 10+ | 11.99 | 1 | https://www.amazon.com/AUSTOR-Lengths-Assorted-Preformed-Breadboard/dp/B07CJYSL2T
Custon Jumper MF | Adafruit | 40 | 80 | 2.95 | 2 | https://www.adafruit.com/product/3633 | 2/full system; optional, faster assembly
Custon Jumper MM | Adafruit | 40 | 40 | 3.95 | 1 | https://www.adafruit.com/product/3142 | 1/full system; optional, faster assembly
Small Single Row Wire Housing Pack for DIY Jumper Cables | Adafruit | 50 |  | 1.95 | 1 | https://www.adafruit.com/product/3145 | 1/full system; optional, faster assembly
Large Dual Row Wire Housing | Adafruit | 50 |  | 3.95 | 1 | https://www.adafruit.com/product/3144 | 1/full system; optional, faster assembly
Small Dual Row Wire Housing | Adafruit | 50 |  | 1.95 | 1 | https://www.adafruit.com/product/3143 | 1/full system; optional, faster assembly
Ø1/2" Pedestal Post Holder | ThorLabs | 1 | 4 | 25.97 | 4 | https://www.thorlabs.com/thorproduct.cfm?partnumber=PH2E#ad-image-0 | Can replace with 3d printed version
Clamping Fork | ThorLabs | 1 | 4 | 11.69 | 4 | https://www.thorlabs.com/thorproduct.cfm?partnumber=CF125C/M#ad-image-0 | Can replace with 3d printed version
5V/2A Adapter | Amazon | 1 | 1 | 8.99 | 1 | https://www.amazon.com/100-240V-5-52-5mm-Transformer-Electronic-Equipment/dp/B0863J9RLW | for servos
24V/2A Adapter | Amazon | 1 | 1 | 11.9 | 1 | https://www.amazon.com/ALITOVE-Supply-Adapter-100-240V-Converter/dp/B07VKSYXDW?s=electronics | for solenoids
DC Power Pigtail | Amazon | 10 | 2 | 9.49 | 1 | https://www.amazon.com/43x2pcs-Connectors-Security-Lighting-MILAPEAK/dp/B072BXB2Y8
Solenoid | Parker | 1 | 1 | 96 | 1 | https://ph.parker.com/us/12051/en/series-3-miniature-inert-liquid-valve/003-0257-900 | inconsistent lead time, 1 / solution
5.6k Ohm Resistors (solenoids) | Amazon | 100 | 1 | 5.95 | 1 | https://www.amazon.com/Projects-100EP5145K60-5-6k-Resistors-Pack/dp/B0185FI2RE?s=gateway | 1/ solution
Tip 120 Transistor | Amazon | 12 | 1 | 7.15 | 1 | https://www.amazon.com/STMicroelectronics-TIP120-Power-Darlington-Transistor/dp/B06ZY654XN?hvadid=200173223500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 | 1/ solution
Diode 1N4007 | Amazon | 125 | 1 | 5.99 | 1 | https://www.amazon.com/BOJACK-Rectifier-IN4007-Electronic-Silicon/dp/B07Q6J9TNW | 1/ solution
Heat Shrink Tubing (1/8") | Amazon | 100' | 1 | 15.8 | 1 | https://www.amazon.com/Heat-Shrink-Tubing-1-100FT-Black/dp/B00FL4JO7U?s=gateway
Heat Shrink Tubing (3/4") | Amazon | 10' | 1 | 13.88 | 1 | https://www.amazon.com/Heat-Shrink-Tubing-1-100FT-Black/dp/B01BZDZZ0U?s=gateway
Ester-Based Tubing | United States Plastic Corp | 1 | 5 | 1.5 | 5 | https://www.usplastic.com/catalog/item.aspx?catid=717&itemid=66285 | ~5ft/solenoid
Rotary Encoder (Kubler) | RS Components | 1 | 1 | 178.85 | 1 | https://export.rsdelivers.com/product/kubler/05240011221024/incremental-encoder-kubler-05240011221024-1024/4314599?matchtype=&pla-681970267105&gclsrc=aw.ds | inconsistent lead time
Lego Wheel | Lego | 1 | 1 | 2 | 1 | https://www.bricklink.com/v2/catalog/catalogitem.page?P=86652c01#T=S&O={%22iconly%22:0} | price varries according to seller (alternative: https://www.aliexpress.us/item/3256801362940364.html?acnt=708-803-3821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
Straight Hose Barb Union | Masterflex | 25 | 2 | 33.25 | 1 | https://www.coleparmer.com/i/masterflex-fitting-polypropylene-straight-hose-barb-union-1-16-id-25-pk/0636511 | 2 / solution
Elbow Hose Barb Union | Masterflex | 25 | 1 | 53.5 | 1 | https://www.coleparmer.com/i/masterflex-fitting-clear-polypropylene-elbow-hose-barb-union-1-16-id-25-pk/0636517 | For radial multi spout
Solder | Amazon | 1 | 1 | 9.99 | 1 | https://www.amazon.com/MAIYUM-63-37-Solder-Electrical-Soldering/dp/B076QF1Y85?s=industrial
JB weld | Amazon | 1 | 1 | 8.28 | 1 | https://www.amazon.com/J-B-Weld-8265S-Reinforced-Hardener/dp/B00YNJ2XAE?s=industrial | used with soldered arduino case
Super Glue | Amazon | 1 | 1 | 2.86 | 1 | https://www.amazon.com/Loctite-Liquid-10-Gram-Longneck-234796/dp/B0002YXG78?s=industrial | used with micropositioner / soldered arduino case
Lubricant | Amazon | 1 | 1 | 4.77 | 1 | https://www.amazon.com/Super-Lube-51004-Synthetic-Viscosity/dp/B000UKUHXK | used with linear actuator
#6-32 Machine Screw 4" | Grainger | 100 | 2 | 11.95 | 1 | https://www.grainger.com/product/FABORY-6-32-Machine-Screw-1MY76?searchBar=true&searchQuery=%2525231MY76 | used with micropositioner / soldered arduino case
#6-32 Machine Screw 3" | Grainger | 100 | 1 | 6.45 | 1 | https://www.grainger.com/product/FABORY-6-32-Machine-Screw-1MY75?searchBar=true&searchQuery=%2525231My75 | used with micropositioner / soldered arduino case
#6-32 nut | Grainger | 100 | 6 | 2.89 | 1 | https://www.grainger.com/product/GRAINGER-APPROVED-Hex-Nut-2GA55?searchBar=true&searchQuery=%2525232GA55 | used with micropositioner / soldered arduino case
#2-56 Machine Screw 1/2" | Grainger | 100 | 1 | 1.18 | 1 | https://www.grainger.com/product/FABORY-2-56-Machine-Screw-1ME91 | used with micropositioner / soldered arduino case
#2-56 nut | Grainger | 100 | 1 | 1.74 | 1 | https://www.grainger.com/product/GRAINGER-APPROVED-Hex-Nut-2FE43?searchBar=true&searchQuery=%2525232FE43 | used with micropositioner / soldered arduino case
10mL Syringes w/ Lure Lock | Amazon | 15 | 5 | 10.99 | 1 | https://www.amazon.com/Buytra-Graduated-Measuring-Refilling-Dispensing/dp/B07FCHZY5Q
computer | various | 1 | 1 | ? | 1
magnets (3/16" cube) | Applied Magnets | 1 | 4 | 0.15 | 4 | https://www.magnet4less.com/rare-earth-magnets-n42-3-16-inch-strong-neodymium-cubes | optional for magnetic mounts / lids
Museum Putty | Amazon | 1 | 1 | 3.97 | 1 | https://www.amazon.com/Quakehold-88111-Museum-Putty-Neutral/dp/B0002VA9NA
BD Blunt Fill Needle (40mm) | Net32 | 100 | 10 | 24.63 | 1 | https://app.quartzy.com/groups/178614/products/157382 | 2/ solution
BNC Female | Amazon | 5 | 5 | 9.99 | 1 | https://www.amazon.com/Hxchen-Female-Bulkhead-Insulated-Connector/dp/B07V1SWM9J
Dremel EZ456B | Amazon | 12 | 1 | 20.97 | 1 | https://www.amazon.com/Dremel-EZ456B-2-Inch-Rotary-Cut-Off/dp/B000FBLRVU
M3 screws | Amazon | 1110 | 1 | 20.01 | 1 | https://www.amazon.com/1110pcs-Stainless-Washers-Assortment-Precise/dp/B08YYZSZVP | variety pack
Cat6 breakout (optional) | Amazon | 4 | NA | 12.99 | NA | https://www.amazon.com/risingsaplings-Connector-cBreakout-Compatible-Ethernet/dp/B08XB8G52H | optional cat6 adapter
DB25 female (optional) | Amazon | 25 | NA | 13.95 | NA | https://www.amazon.com/Pc-Accessories-Connectors-Connector-25-PACK/dp/B073P46MXW?s=electronics | optional DB25 adapter

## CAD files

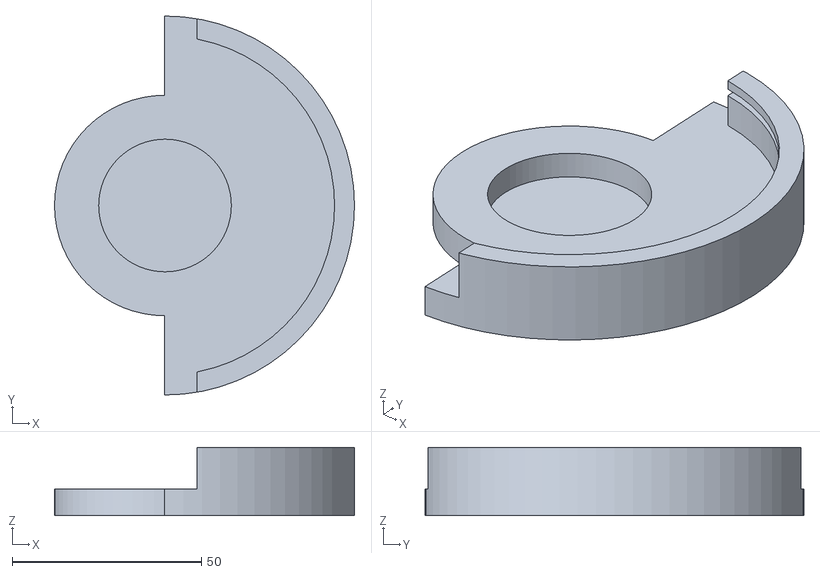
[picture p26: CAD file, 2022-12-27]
3d_models/multi_spout_assembly_guide.stl
79.2 x 100.0 x 18.0

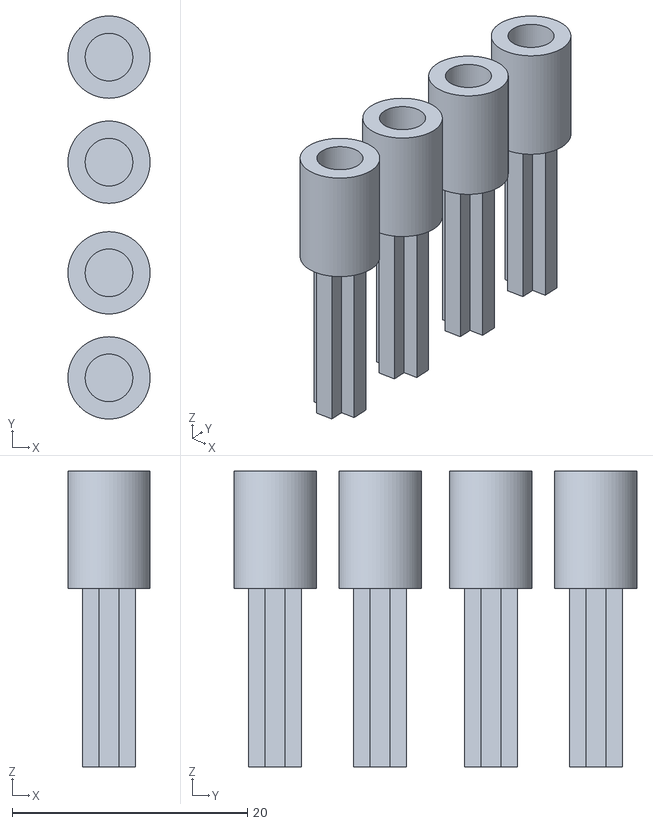
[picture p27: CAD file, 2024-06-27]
3d_models/rotaryencoder_to_wheel_adapter.stl
7.00 x 34.3 x 25.1

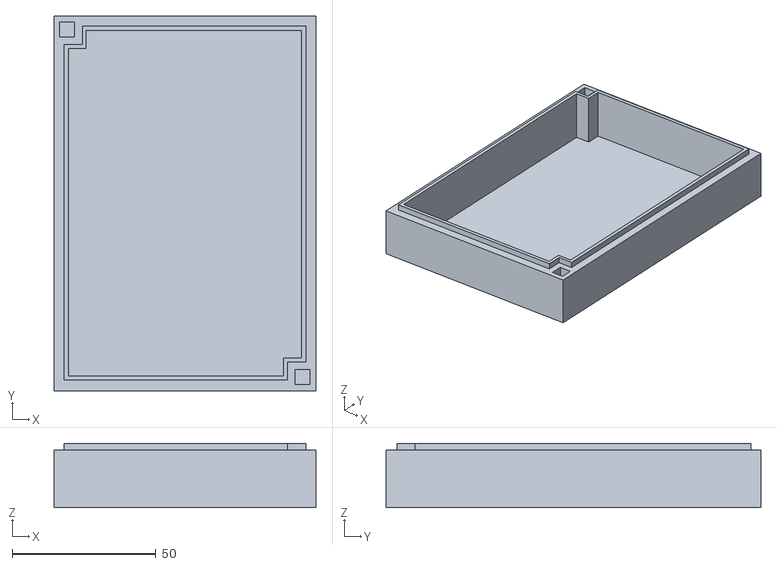
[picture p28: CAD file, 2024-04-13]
3d_models/voltage_lick_detector_enclosure_top.stl
91.0 x 130.2 x 22.4

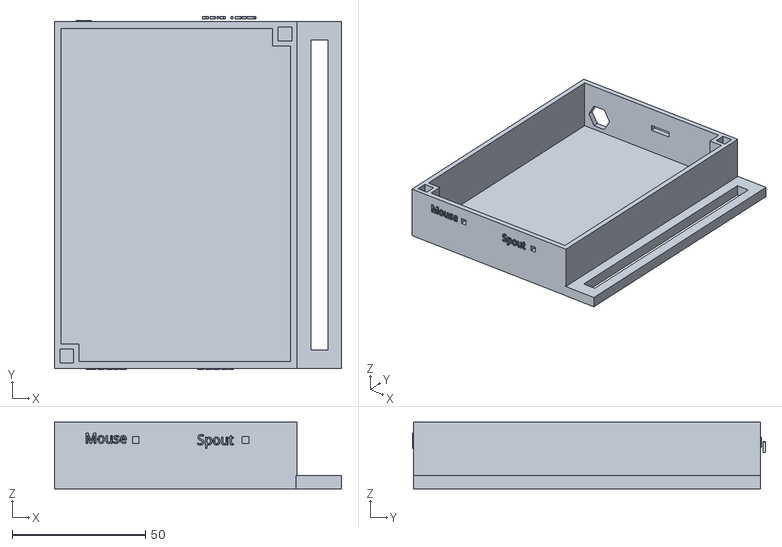
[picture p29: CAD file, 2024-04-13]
3d_models/voltage_lick_detector_enclosure_bottom.stl
107.6 x 132.5 x 25.0

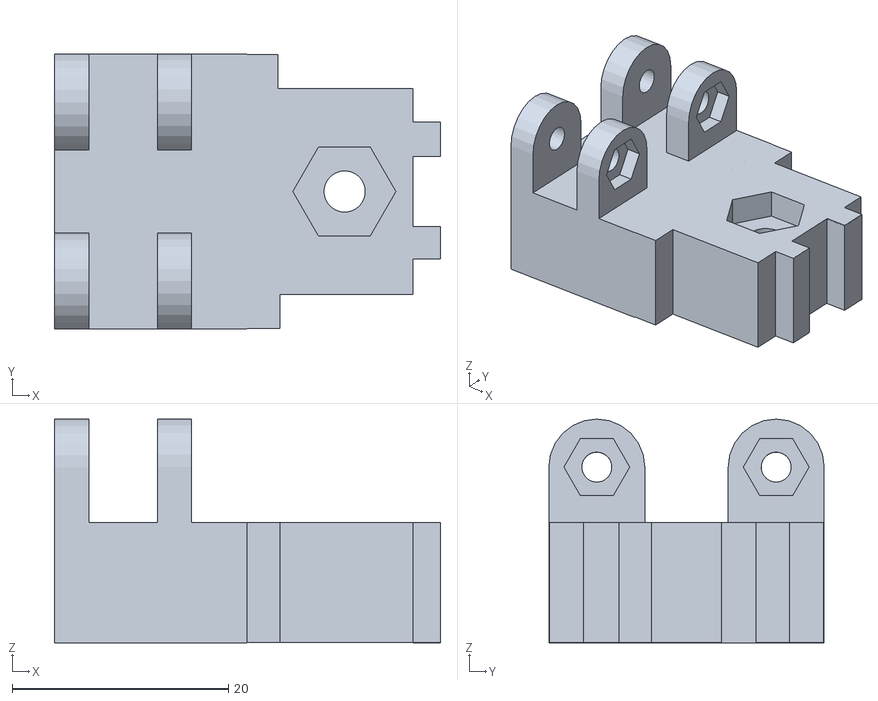
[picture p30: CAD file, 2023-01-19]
3d_models/micropositioner_zadapter.stl
35.7 x 25.5 x 20.7

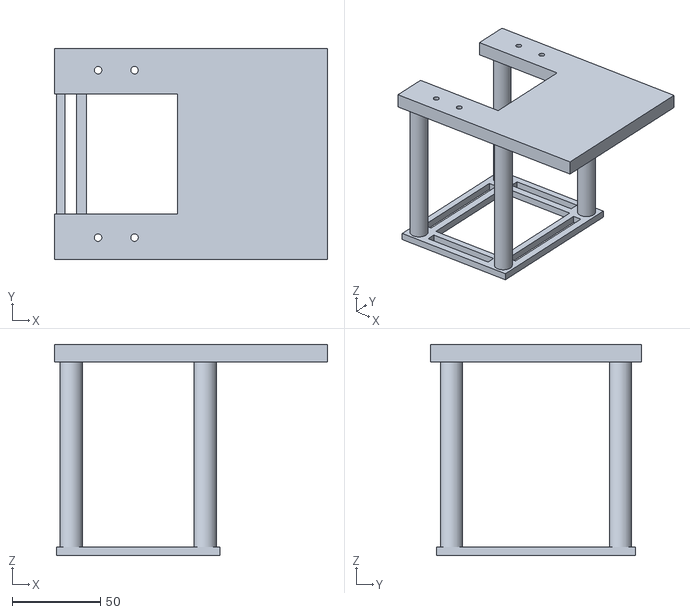
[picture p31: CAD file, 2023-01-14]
3d_models/headfixation_stage_with_posts.stl
155.1 x 120.0 x 120.0

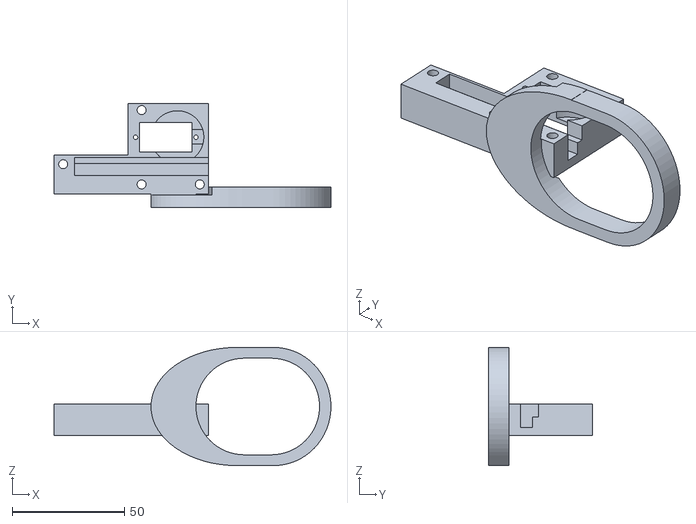
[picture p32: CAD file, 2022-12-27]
3d_models/linear_actuator_pbody_multispout.stl
123.3 x 46.3 x 52.6

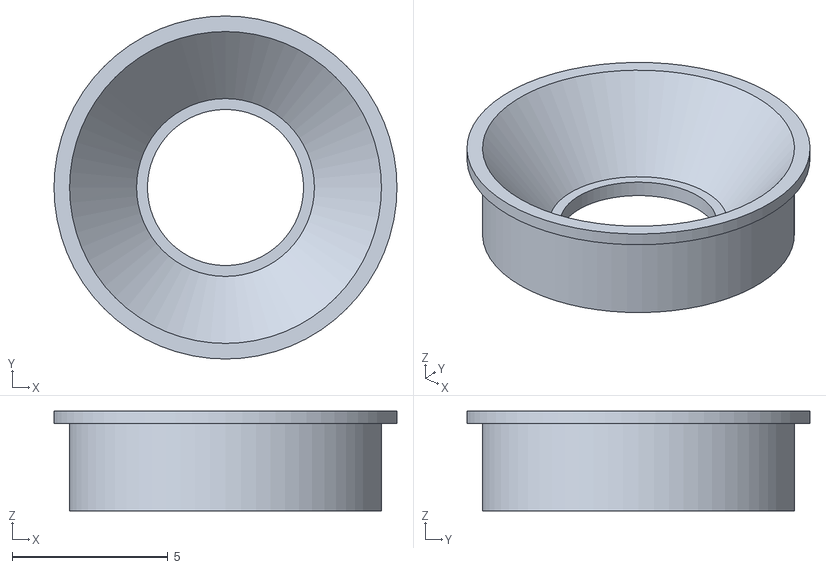
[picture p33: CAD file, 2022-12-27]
3d_models/headring.stl
11.0 x 11.0 x 3.20

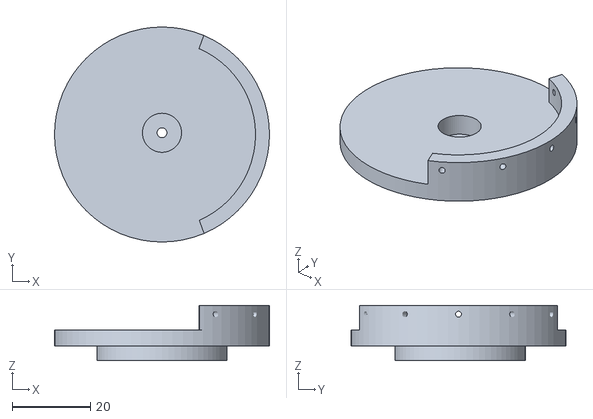
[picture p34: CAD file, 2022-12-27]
3d_models/multi_spout_head.stl
55.0 x 55.0 x 14.2

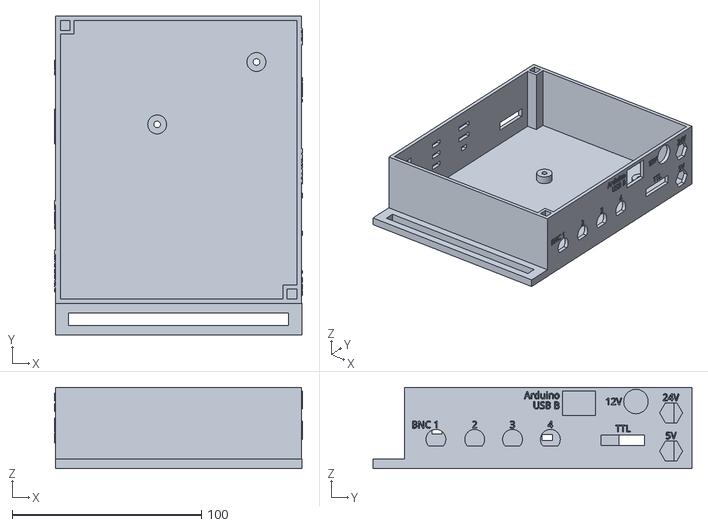
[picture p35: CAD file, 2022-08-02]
3d_models/arduino_case_bottom.stl
131.1 x 168.6 x 43.0

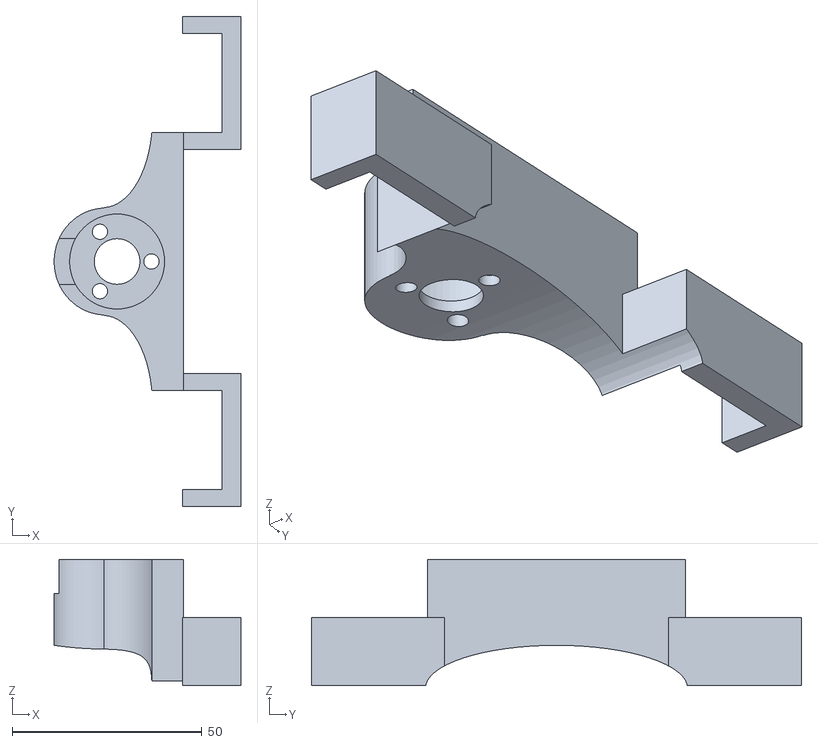
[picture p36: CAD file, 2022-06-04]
3d_models/stage_to_rotaryencoder_adapter_tall.stl
49.2 x 129.0 x 33.3

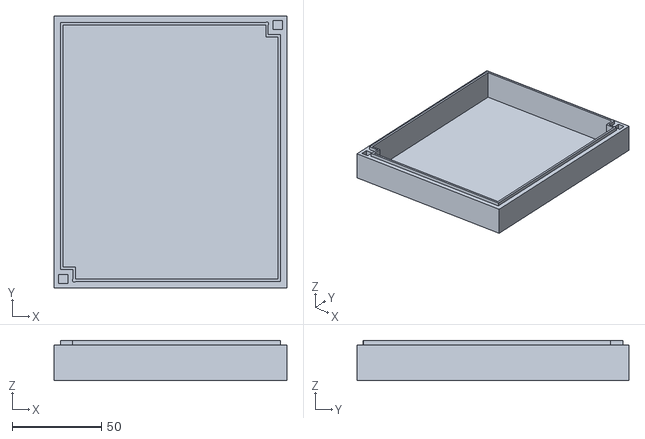
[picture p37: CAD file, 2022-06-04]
3d_models/arduino_case_top.stl
130.0 x 152.0 x 22.4

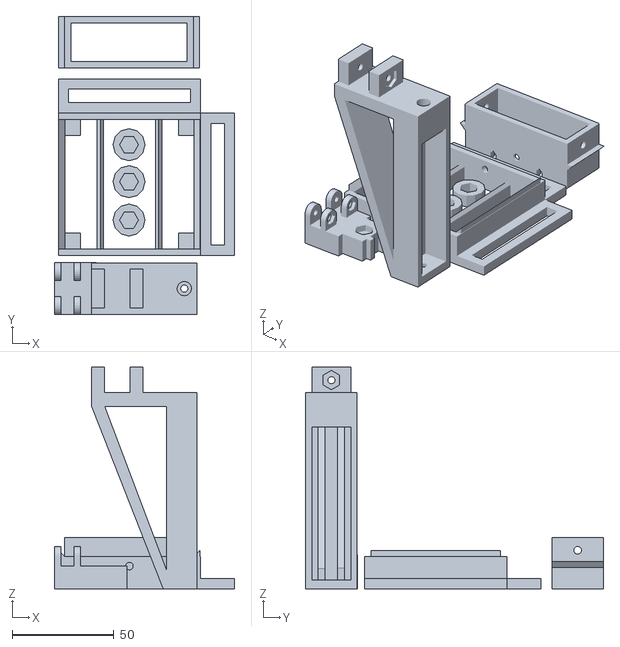
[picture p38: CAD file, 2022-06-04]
3d_models/micropositioner_combined.stl
88.4 x 146.4 x 108.9

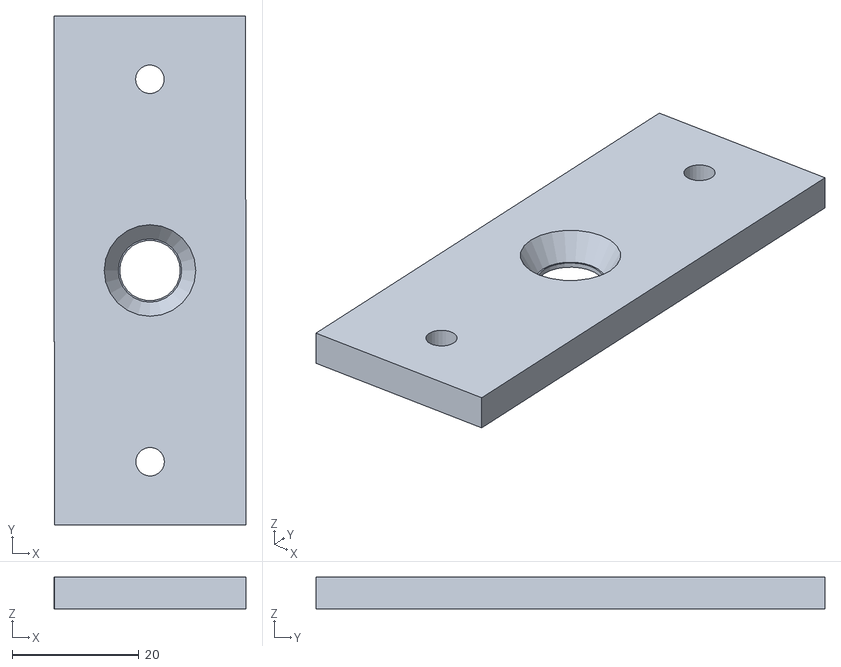
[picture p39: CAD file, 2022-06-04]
3d_models/headfixation_toppiece.stl
30.3 x 80.3 x 5.00

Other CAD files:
3d_models/mount_solenoid_x5.stl
3d_models/micropositioner_zframe.stl
3d_models/stage_to_wheelbrake_servo_adapter.stl
3d_models/mount_10mL_x6.stl
3d_models/brake_bar.stl
3d_models/headfixation_conicalmount.stl
3d_models/headfixation_plate.stl
3d_models/headfixation_stage.stl
3d_models/linear_actuator_combined.stl
3d_models/linear_actuator_cover.stl
3d_models/linear_actuator_helicalgear.stl
3d_models/linear_actuator_pbody_singlespout.stl
3d_models/linear_actuator_rackbody_multispout.stl
3d_models/linear_actuator_rackbody_singlespout.stl
3d_models/linear_actuator_rackspur.stl
3d_models/micropositioner_knob.stl
3d_models/micropositioner_xframe.stl
3d_models/micropositioner_yframe.stl
3d_models/mount_10mL_x2.stl
3d_models/mount_solenoid_x2.stl
3d_models/stage_to_rotaryencoder_adapter_short.stl
3d_models/stage_to_rotaryencoder_adapter_standard.stl

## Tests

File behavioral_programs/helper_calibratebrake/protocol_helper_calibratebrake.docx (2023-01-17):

Protocol for helper_opensol.io

Program purpose: helper_calibratebreak.io allows users to test multiple break angles to determine the ideal angle for locking the wheel

Use Instructions:

1) Open the program (make sure the program is located in a folder of the same name)
2) Set the parameters and pins

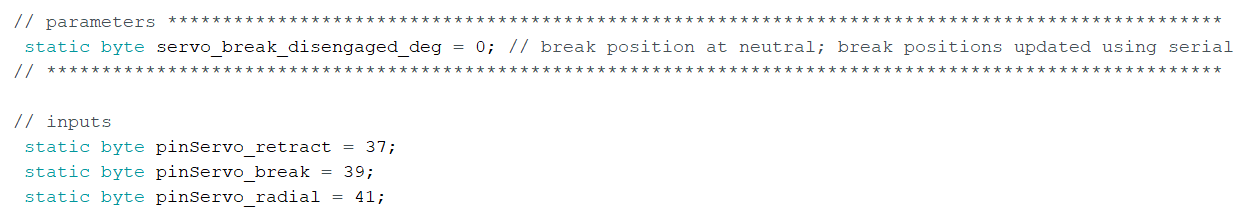
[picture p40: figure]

- It is fine if you do not have all 3 servos, so long as nothing is connected to those pins
- Note: servobreak_disengaged_deg is the angle of the servo at the resting (UP) position. This position is the starting position for each of the break engagements
3) Upload script to arduino by clicking the “Upload” arrow button on the top left corner
4) Open the serial monitor by clicking the “Serial Monitor” button on the top right corner

You should then be presented with this screen:

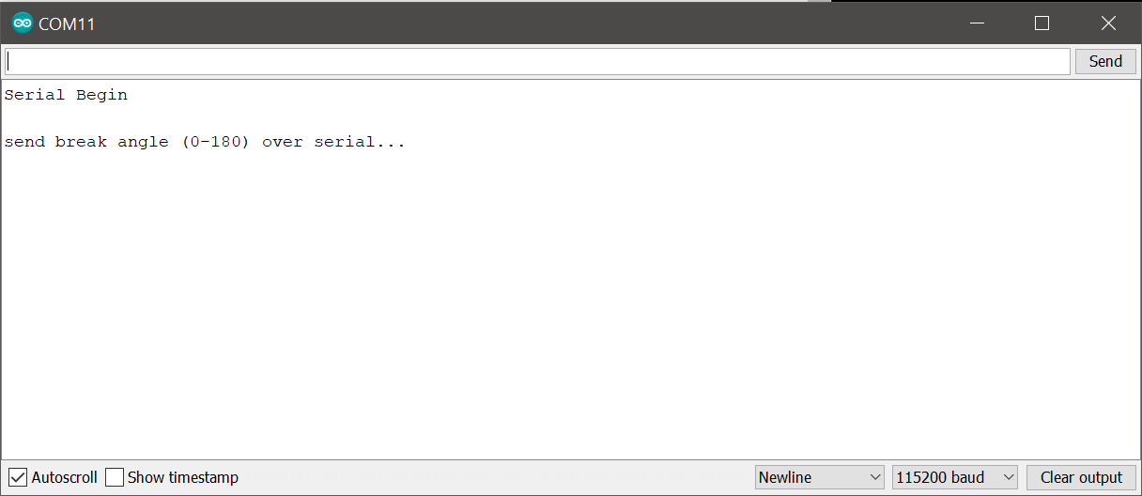
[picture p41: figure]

Note: if you do not see this text printed in the serial monitor, see troubleshooting arduino software document

5) Starting with low values (~10) and working up to high values (~30+), enter the break degree you wish to test and send to arduino
  a) Typically, angles 15-25 will work well.

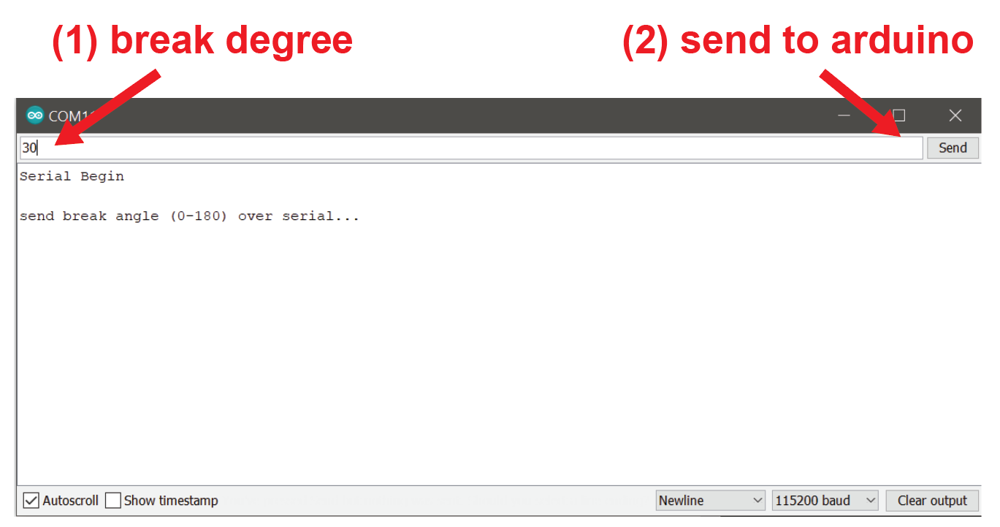
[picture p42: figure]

6) The break will engage and remain engaged at the input angle

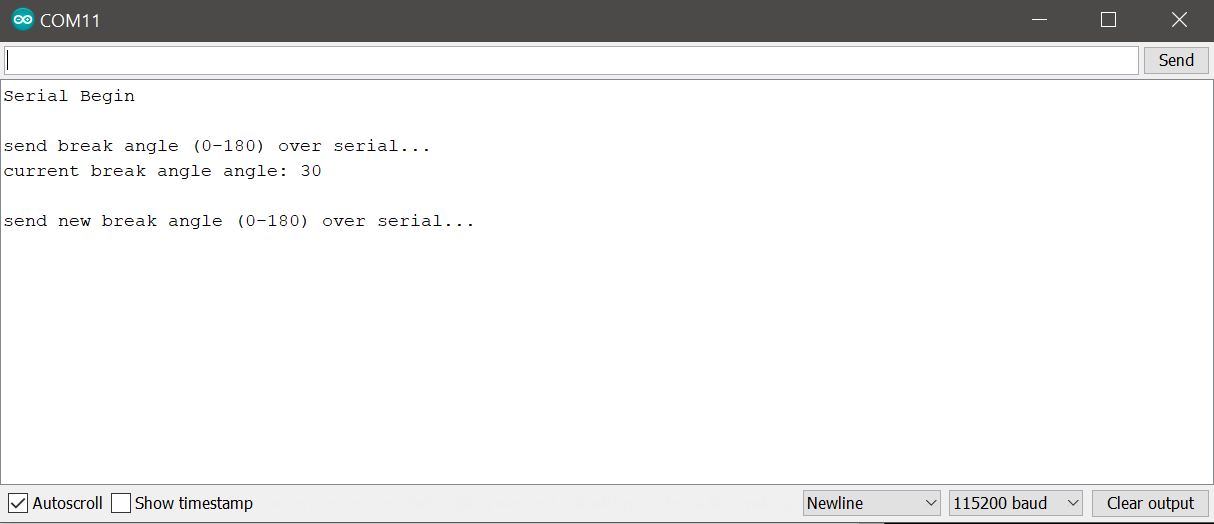
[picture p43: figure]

Note: the serial monitor should show the current angle of the break servo

7) Check to see if the wheel is able to rotate. If the wheel spins freely, increase the angle by 5 and send again over serial. Repeat this process until you have a break angle that is strong enough to keep the wheel stable with mild force applied by finger. Record the final break angle value for future use.

Note: ideally, the wheel should only rotate with moderate force. However, do not use an angle larger than you need, as this can cause damage to the wheel to stage adapter and generate unnecessary noise. If you notice that the mouse is able to rotate the wheel when it should be breaked, increase the break angle.

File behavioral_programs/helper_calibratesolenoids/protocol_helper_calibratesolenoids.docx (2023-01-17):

Protocol for helper_opensol.io

Program purpose: helper_calibratesolenoids.io allows users to run a calibration sequence to estimate the volume of each sol opening period.

Note: default program is setup for a target volume of 200µL total, 1.5µL per sol opening

Preparation Instructions:

1) Prior to following the “Use Instructions”, fill the solution line by following the protocol_helper_opensol instructions.
2) If measuring volume directly: obtain a centrifuge tube that has a volume marker for 200µL.
3) If measuring volume using weight: obtain and record the weight in a small weigh boat.

Use Instructions:

1) Open the program (make sure the program is located in a folder of the same name).
2) Set the parameters and pins.

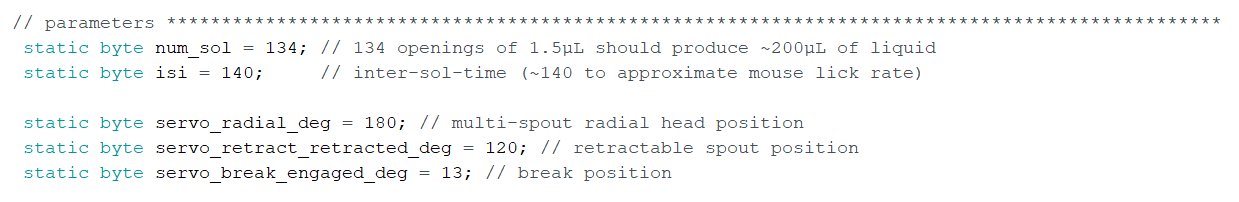
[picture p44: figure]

- It is fine if you do not have all 3 servos, so long as nothing is connected to those pins.
3) Upload script to arduino by clicking the “Upload” arrow button on the top left corner
4) Open serial monitor by clicking the “Serial Monitor” button on the top right corner

You should then be presented with this screen:

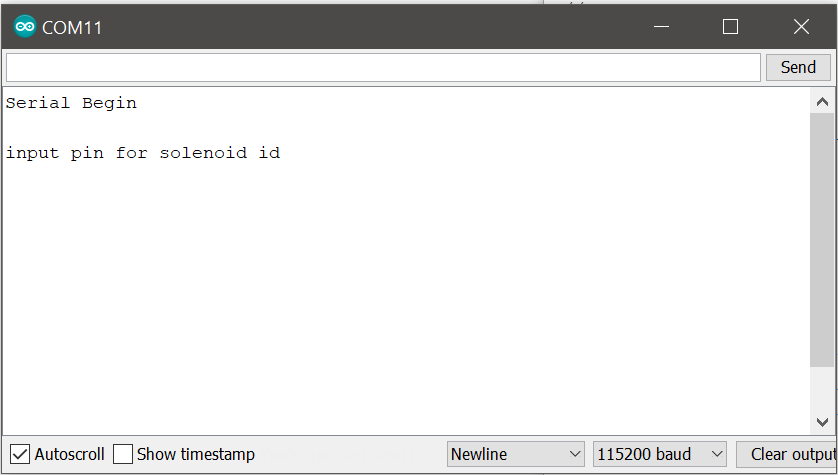
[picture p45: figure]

Note: If you do not see this text printed in the serial monitor, see troubleshooting arduino software document.

5) Enter the pin number for solenoid into the text box to the left of the “Send” button and then click the button to send the value over serial.

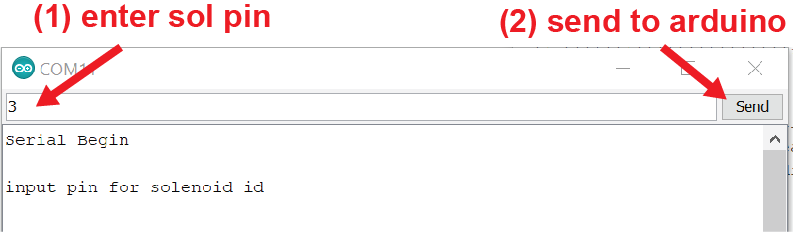
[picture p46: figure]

6) Prepare to collect the solution by holding the centrifuge tube or weigh boat under the spout.
7) Enter sol duration into the text box and send value over serial.

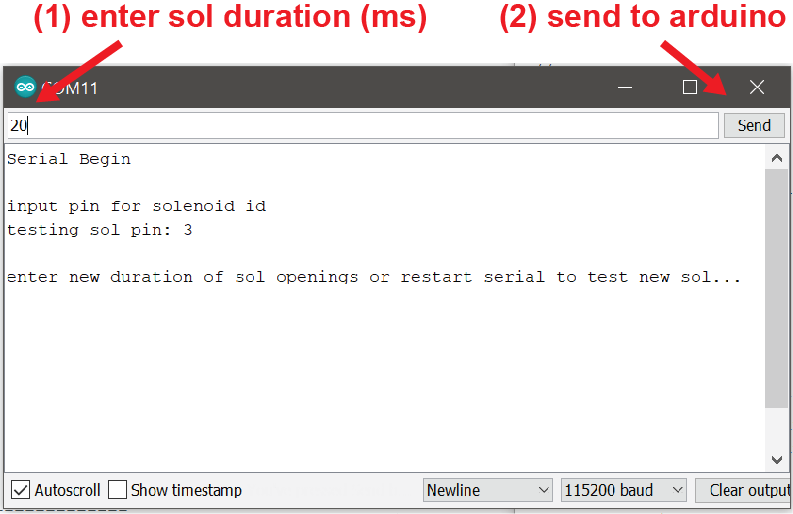
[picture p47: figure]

At the start of the sequence, the arduino will print the current parameters. At the end of the sequence, the arduino will indicate that the sequence is complete and prompt you for a new solenoid duration.

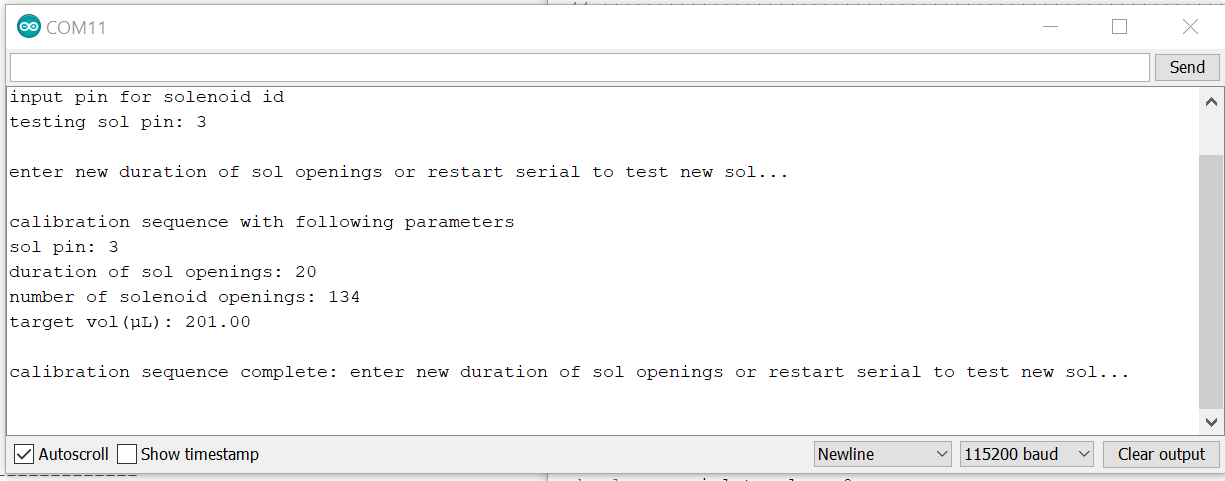
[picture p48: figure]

8) Collect and measure the liquid delivered throughout the calibration sequence.
  a) Check volume by referencing the volume markers on the centrifuge tube or
  b) Weigh the weigh boat containing the liquid and subtract out the weight of the weigh boat alone.
9) If you are off your target (200µL) redo previous steps with a new sol duration based on the volume obtained (If the volume is higher than intended, reduce the sol open duration; if the volume is lower than intended, increase the sol open duration).
10) Once you have calibrated the current spout, save the open sol duration for future reference as you will need this value for each of the arduino scripts used for behavior.
11) Repeat the above steps for each solenoid for the system. To set a new spout, close and reopen the serial monitor.

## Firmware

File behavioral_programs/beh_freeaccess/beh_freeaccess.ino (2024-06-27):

/*
-General notes--------------------------
* This program is a spout training task, where each lick triggers a solenoid opening
* brake is engaged, spout is extended, and multi-spout head is rotated at start of session
* spout is retracted at end of session
* setup to accomodate setups with multiple spouts
  ~ see section spout / sol pins & parameters, fill out 1 element per spout on system

-Dependencies---------------------------
This program uses multiple dependencies (see protocol: for instructions on installation)
* Servo.h: library used to control micro servos used for brake / retractable spout 
* Wire.h: library used for capacitive touch sensor
* Adafuit_MPR121.h: library used for capacitive touch sensor

-Data structure-------------------------
* see general arduino program approach for a description of how events and parameters are recorded

-Running the program--------------------------
* follow protocol for behavior script

*/

// dependencies
  #include <Wire.h>
  #include "Adafruit_MPR121.h"
  #include <Servo.h>

// session parameters *************************************************************************************************************
 // general parameters -------
  static unsigned long session_duration = 600000; // session duration (ms) (note: do not use formula here)
  static byte lick_detection_circuit = 0; // 0: cap sensor, 1: voltage sensor
  static int tm_lick_latency_min = 50;

 // spout / sol pins & parameters
  static byte num_spouts = 5; // should have this many values for each of the following vectors

  // spout vectors (each element will correspond to a spout, add or remove elements based on system, default is setup for 5 spouts)
  static byte pinSol[] =                      {  4,  5,  6,  7,  8};
  static byte sol_duration[] =                { 30, 30, 30, 30, 30}; // calibrate to ~1.5µL / delivery
  static byte servo_radial_degs [] =          {  0, 30, 60, 90,120};
  static byte servo_retract_extended_degs[] = {180,180,180,180,180};
  static byte pinLickometer_ttl[] =           { 22, 22, 22, 22, 22};
  
  byte current_spout = 1; // set spout for session (1 to n, where n is the number of spouts on the system; used to index each vector above)

// arduino pins ----------------------------------------------------------------------------
 // inputs ----------------------------
  static byte pinLickometer = 21; // only set to output if lick_detection_circuit = 1
  
 // outputs ---------------------------
  static byte pinServo_retract = 9; 
  static byte pinServo_brake = 10;
  static byte pinServo_radial = 11;

  // ttls for external time stamps
  static byte pinSol_ttl = 23; // single output used for all solenoid onset

//capacitance sensor variables -------------------------------------------------------------
  Adafruit_MPR121 cap = Adafruit_MPR121();
  uint16_t lasttouched = 0;
  uint16_t currtouched = 0;

// servo brake variables / parameters ------------------------------------------------------
  Servo servo_brake;  // create servo object to control a servo
  static byte servo_brake_engaged_deg = 15;

// servo retractable spout variables / parameters ------------------------------------------
  Servo servo_retract;
  static byte servo_retract_retracted_deg = 160;
  unsigned long ts_servo_retract_retracted;

// servo radial variable / parameters-------------------------------------------------------
  Servo servo_radial;
  
// flags -------------------------------------------------------------------------------------
 // variables---
  boolean lick;
  boolean lick_gate = 1;
  boolean pinLickometer_state;
  boolean pinLickometer_state_previous;
  
// time stamps & timers ---------------------------------------------------------------------
 // variables---
  volatile unsigned long ts; 
  unsigned long ts_start;
  unsigned long ts_sol_offset;
  unsigned long ts_sol_ttl_off;
  unsigned long ts_lickomter_ttl_off; 
  unsigned long ts_lick_gate_open = 0;
  unsigned long session_end_ts;

 // parameters---
  static int ttl_duration = 5; // duration of ttl pulses for external time stamps (ms)


// _______________________________________________________________________________________________________________________________________________________________________________
/// setup ________________________________________________________________________________________________________________________________________________________________________
void setup() {
  Serial.begin(115200);
  
 // define inputs
  if(lick_detection_circuit == 1){
    pinMode(pinLickometer, INPUT);
  }
  
 // define outputs
  pinMode(pinSol_ttl, OUTPUT);
  pinMode(pinServo_retract, OUTPUT);
  pinMode(pinServo_brake, OUTPUT);  
  pinMode(pinServo_radial, OUTPUT); 

  for (uint8_t i_sol = 0; i_sol < num_spouts; i_sol++) { // for each solenoid
    pinMode(pinSol[i_sol], OUTPUT);                       // define sol as output
    pinMode(pinLickometer_ttl[i_sol], OUTPUT);           // 
  } 

 // engage servo brake prior to session start
  servo_brake.attach(pinServo_brake); 
  Serial.print(11); Serial.print(" "); Serial.println(ts);      
  servo_brake.write(servo_brake_engaged_deg);
  delay(250);
  servo_brake.detach();

 // rotate multi-spout head prior to session start
  servo_radial.attach(pinServo_radial);
  servo_radial.write(servo_radial_degs[current_spout-1]);
  Serial.print(130); Serial.print(" "); Serial.println(ts);            delay(3);   // print radial position moved
  Serial.print(127); Serial.print(" "); Serial.println(ts);            delay(3);
  Serial.print(127); Serial.print(" "); Serial.println(current_spout); delay(3);
  delay(250);
  servo_radial.detach();
 
 // fully extend spout prior to session start
  servo_retract.attach(pinServo_retract); 
  Serial.print(13); Serial.print(" "); Serial.println(ts);      
  servo_retract.write(servo_retract_extended_degs[current_spout]);
  delay(250);
  servo_retract.detach();

  // setup capacitive touch sensor 
  if(lick_detection_circuit == 0){
    if (!cap.begin(0x5A)) {                   // if the sensor is not detected
      Serial.println("MPR121 not detected!"); // print warning (and intentionally crash python program)
      while (1);
    }
    cap.setThresholds(6,2); // set thresholds for cap sensor, adjust these based on sensitivity
    delay(50);
    Serial.print(998);   Serial.print(" "); Serial.println(cap.filteredData(1)); // print cap sensor starting value
  } else {
    delay(50);
  }

 // wait for serial command before initating session---------------------------------------------------------------------
  while (Serial.available() <= 0) {} // wait for serial input to start session
  delay(100);
  
 // save start time and send ttl to initate scope
  ts_start = millis();  
}


/// void loop ____________________________________________________________________________________________________________________________________________________________________
// _______________________________________________________________________________________________________________________________________________________________________________
void loop() {
// background functions (run constantly independent of task events)--------------------------------------------
 // generate timestamp ---------------------------
  ts = millis()-ts_start;

  // open lick gate -------------------------------
  if (ts > ts_lick_gate_open && ts_lick_gate_open != 0) {
    lick_gate = 1;
    ts_lick_gate_open = 0;
  }
  
 // close solenoids---------------------------
  if (ts >= ts_sol_offset && ts_sol_offset != 0) {           // if time is after solenoid offset time
    digitalWrite(pinSol[current_spout - 1], LOW);              // set state to low
    Serial.print(14); Serial.print(" "); Serial.println(ts); // print sol offset
    ts_sol_offset = 0;                                       // reset solenoid offset time to close if statement
  }

 // turn off ttls for external time stamps ------------------------
  // lick---
  if (ts >= ts_lickomter_ttl_off && ts_lickomter_ttl_off != 0) {
    digitalWrite(pinLickometer_ttl[current_spout-1], LOW); // write ttl low
    ts_lickomter_ttl_off = 0;            // reset off time to close if statement
  }
  
 // solenoid---
  if(ts>=ts_sol_ttl_off && ts_sol_ttl_off!=0){
    digitalWrite(pinSol_ttl,LOW);  // write ttl low
    ts_sol_ttl_off = 0;            // reset off time to close if statement
  }
  
// session initialization (runs once at start) -----------------------------------------------------------------
  if(session_end_ts == 0){
    Serial.print(1);   Serial.print(" "); Serial.println(ts);                          // print start session
    Serial.print(100); Serial.print(" "); Serial.println(session_duration);            // print session duration
    Serial.print(116); Serial.print(" "); Serial.println(sol_duration[current_spout-1]); // print sol_duration

    session_end_ts = ts + session_duration;
  }


// licking-----------------------------------------------------------------------------------------------------
 if(lick_detection_circuit == 0){ // if using cap sensor --------------------------------------------------------------
   // check state of sensor to see if it is currently touched
    currtouched = cap.touched(); 
  
    // check to see if touch onset occured
    if ((currtouched & _BV(current_spout)) && !(lasttouched & _BV(current_spout)) ) { // if touched now but not previously
      lick = current_spout;                                                           // flag lick
    }
  
   // save current state for comparison with next state
    lasttouched = currtouched; 
 }

 if(lick_detection_circuit == 1){ // if using voltage sensor ----------------------------------------------------------
  // check state of sensor to see if it is currently touched
   pinLickometer_state = digitalRead(pinLickometer);

  // check to see if touch onset occured
   if(pinLickometer_state > pinLickometer_state_previous) { // if touched now but not previously
        lick = current_spout+1;                             // flag lick
   }
   
  // save current state for next loop 
   pinLickometer_state_previous = pinLickometer_state;
 }

 // programmed consequences to licking
  if (lick > 0) { // if lick has occurred
    if(lick_gate){      
      digitalWrite(pinLickometer_ttl[current_spout - 1], HIGH);                          // turn on ttl for external ts
      Serial.print(30 + current_spout); Serial.print(" "); Serial.println(ts); // print lick onset
      ts_lickomter_ttl_off = ts + ttl_duration;                       // set ttl offset time
  
      digitalWrite(pinSol[current_spout - 1], HIGH);                                    // open solenoid for touched spout
      Serial.print(40 + current_spout); Serial.print(" "); Serial.println(ts); // print sol opening onset
      ts_sol_offset = ts + sol_duration[current_spout - 1];                    // set solenoid close time
    }

    lick_gate = 0; // close lick gate until tm_lick_latency_min ms have passed

    if (tm_lick_latency_min > sol_duration[lick - 1]) {
      ts_lick_gate_open = ts + tm_lick_latency_min;
    } else {
      ts_lick_gate_open = ts +  sol_duration[lick - 1];
    }

    lick = 0; // reset lick flag to close if statement
    
  }

 // session termination ---------------------------------------------------------------------------------------------------
  // end session if end time is reached
  if(ts > session_end_ts && session_end_ts != 0){
    fun_end_session();
    Serial.print(99); Serial.print(" "); Serial.println(ts);    // print end of session  
  }
}
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

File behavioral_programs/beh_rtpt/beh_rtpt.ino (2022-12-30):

/*
-General notes--------------------------
* This program is a real-time place testing program (rtpt)
* The wheel is divided into 2 zones based on the starting position of the wheel
* location in one zone sets external ttl to high, the other zone sets to low
* options for pairing tones with the two zones 
* options for switching contingency during session

-Dependencies---------------------------
This program uses multiple dependencies (see protocol: for instructions on installation)
* Servo.h: library used to control micro servos used for brake / retractable spout 

-Data structure-------------------------
* see general arduino program approach for a description of how events and parameters are recorded

-Running the program--------------------------
* follow protocol for behavior script

*/

// dependencies
  #include <Servo.h>

 // parameters 
  unsigned long session_duration = 1200000; // ms

  unsigned long tm_switch_pairing_step = -1; // switch pairing every x ms (-1: no switching)
  unsigned long ts_switch_pairing = 0;

  // zone & tone parameters*************
  int zone = 2;  // initial pairing szone
  
  static boolean session_tone = 1; // 0: no tone for session; 1: tone to indicate paired / unpaired
  unsigned long tone_freq_initially_unpaired = 8000;
  unsigned long tone_freq_initially_paired = 5000;
  //**************************************
  
  int ppr = 1024;
  int rotary_resolution = 16; // 1024PPR total; number of pulses per encoding
  int ppr_encoded = 64; // ppr / rotary_resolution
  
  boolean toggle_pairing = 0; // 
  int ttl_duration = 5; // duration of ttl time stamp (ms)

// arduino pins ----------------------------------------------------------------------------
 // inputs ----------------------------
  static int pinRotaryEncoderA = 3;
  static int pinRotaryEncoderB = 2;
  
 // outputs ---------------------------
  static byte pinServo_retract = 9; 
  static byte pinServo_brake = 10;
  static byte pinServo_radial = 11;
  static byte pinSpeaker = 12;
  
  static byte rotation_left_ttl = 8;
  static byte rotation_right_ttl = 9;
  
  int pinextTTL = 46;

// variables ------------------------- 
  boolean session_pairing_current;
  volatile int rotation_right_counter_trial = 0;  
  volatile int rotation_left_counter_trial = 0;
  
  volatile boolean rotation_right_flag = 0;
  volatile boolean rotation_left_flag = 0;
  
  volatile int rotation_position;
  volatile int rotation_position_prev = rotation_position;

  
  unsigned long ts; 
  unsigned long ts_start;
  unsigned long session_end_ts;
  
 // rotary encoder-------------------------------
  volatile int rotation_right = 0;
  volatile int rotation_right_prev = 0;
  unsigned long rotation_right_ttl_off = 0;
  
  volatile int rotation_left = 0;
  volatile int rotation_left_prev = 0;
  unsigned long rotation_left_ttl_off = 0;
  
  int reading;
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

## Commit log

2022-06-04 added 3d files and images
    [arduino_case_soldered_bottom.stl, arduino_case_top.stl, break_bar.stl, headfixation_conicalmount.stl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]
2022-06-09 added in key_events.csv for decoding arduino data
    directly imported the google sheets file (https://docs.google.com/spreadsheets/d/1e3ltGi7oNBvIpCgUCcZL2Jm8nmv8eVBoPXvdoowNZx4/edit#gid=0)
    Need to reduce down to the events in the programs that will eventually be included
    [key_events.csv]
2022-06-09 added arduino scripts
2022-06-11 moved arduino files to folders
2022-06-17 renamed files updated pre processing functions
    [2021_07_06_aar01.csv, 2021_07_06_aar02.csv, 2021_07_06_aar03.csv, 2021_07_06_aar04.csv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]
2022-06-21 added automated multi-spout processing functions
    [log_data.csv]
2022-06-21 updated example analysis logs
    [log_data.csv, log_multi_spout.csv]
2022-06-22 updates to pre processing and plotting for multi-spout data
    [2022_04_11_abb01.csv, 2022_04_11_abb01_event.csv, 2022_04_11_abb01_param.csv, 2022_04_11_abb03.csv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]
2022-06-22 errors found in data_log
    [2022_04_15_abb05_data_session_binned.csv, 2022_04_15_abb05_data_session_binned_spout.csv, 2022_04_15_abb05_data_spout_summary.csv, 2022_04_15_abb05_data_trial.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]
2022-06-22 errors found in data log
    [2022_05_02_abb05_data_session_binned.csv, 2022_05_02_abb05_data_session_binned_spout.csv, 2022_05_02_abb05_data_spout_summary.csv, 2022_05_02_abb05_data_trial.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]
2022-06-22 new example files produced though processing
    [multi_s_data_lick_proportion.csv, multi_s_data_session_binned_spout.csv, multi_s_data_session_summary.csv, multi_s_data_trial_summary.csv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]
2022-06-22 added comments to combined plot functions
    [multi_nacl_data_lick_proportion.csv, multi_nacl_data_session_binned_spout.csv, multi_nacl_data_session_summary.csv, multi_nacl_data_trial_summary.csv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]
2022-07-28 removed excess
    [2022_04_11_abb01_event.csv, 2022_04_11_abb01_param.csv, 2022_04_11_abb03_event.csv, 2022_04_11_abb03_param.csv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]
2022-08-02 new models andgenerate_trials.py
    [2022_07_01_session_ids_string.csv, arduino_case_bottom.stl, arduino_case_soldered_bottom.stl]
2022-12-03 major reorganization of behavioral_programs folder
    [key_arduinopins.xlsx]
2022-12-06 major edit to beh_training_freeaccess.ino, superficial changes to other arduino scripts
    [key_events.csv]
2022-12-06 edited beh_training_retractablespout
    [key_events.csv]
2022-12-07 edited general note section for retractable spout and operant arduino scripts
2022-12-08 major update to beh_rtpt, minor updates to other arduino scripts
    [key_events.csv]
2022-12-08 added multiple manual arduino scripts for testing hardware
2022-12-08 renamed some files to be more accurate
    [2022_07_01_session_ids_string.csv]
2022-12-09 minor update to beh_operant.ino
    [key_events.csv]
2022-12-10 many small changes
    [2022_12_09_test.csv]
2022-12-10 superficial changes to multispout arduino
2022-12-27 updated assembly instructions and 3d models
    [2022_12_09_test.csv, headring.stl, linear_actuator_pbody_multispout.stl, multi_spout_assembly_guide.stl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]
2022-12-28 update to protocol general and added delays to parameter printing in beh_operant.ino
2022-12-28 update to purchase list
    included knock-off lego wheels from Aliexpress
    [purchase_list.xlsx]
2022-12-29 updated names of files and minor revisions to protocol_assembly.docx
    [brake_bar.stl, stage_to_wheelbrake_servo_adapter.stl]
2022-12-30 "break" to "brake" across all documents and scripts
    [key_arduinopins.xlsx, key_events.csv, purchase_list.xlsx]
2022-12-30 added delays during printing
    An error was found when using some computers where the python script was attempting to access the csv document too quickly while printing the session parameters. I have added a delay of 3ms to each p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
2022-12-30 added analysis templates and added example data for rtpp
    [2021_06_10_aan01.csv, 2021_06_10_aan02.csv, 2021_06_10_aan03.csv, 2021_06_10_aan04.csv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]
2023-01-14 added 3D model for stage w/ posts
    [headfixation_stage_with_posts.stl]
2023-01-18 added photo for multi-spout calibration procedure
2023-01-19 replaced incorrect micropositioner_zadapter.stl file
    [micropositioner_zadapter.stl]
2023-01-25 fixed wiring for rotary encoder diagram in protocol_assembly.docx
2024-04-13 voltage lick detector
    Added protocol for building a voltage lick detector and edited all behavioral programs to support this functionality.
    [voltage_lick_detector_enclosure_bottom.stl, voltage_lick_detector_enclosure_top.stl]
2024-06-11 fixed errors in protocol assembly
    Addressed following errors
    - solenoid circuit resistor text was incorrect (24kOhm -> 5.6kOhm)
    - Labels for TTL arrays #1 and #2 were switched on page 37 and 49
2024-06-27 removed gap in rotaryencoder_to_wheel_adapter
    [rotaryencoder_to_wheel_adapter.stl]
2024-11-25 edited wire guage
    Updated protocol to change wire guage from 23awg to 22awg
2025-02-13 Added diode 1N4007 to circuit
    update to assembly protocol and purchase list to include diode 1N4007 in solenoid circuit. Addition of diode should reduce solenoid disruption of Arduino serial connection.
    [purchase_list.xlsx]
2025-04-30 fixed solenoid circuit text
    text description was incorrect in one portion of protocol (stated the diode was connected to emitter, but should have state it was connected to collector)
